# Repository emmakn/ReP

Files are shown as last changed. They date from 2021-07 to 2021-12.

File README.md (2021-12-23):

# ReP
**Re**petative **P**ipettor

## Background
The ReP was created to automate repetative pipetting tasks in a simple and cost-effective way. It utilizes a rack and pinion design to move the pipette's plunger up and down. It can be calibrated to aspirate and dispense at any given rate, frequency, and volume. It is intended to be held upright with a ring stand clamp or any other clamped arm to allow for easy maneuverability and adaptability. The ReP is built around an Eppendorf pipette. The DC motor is controlled with a Raspberry Pi Nano and an L298N motor controller. The structure itself is 3D printed from PLA.

## Included
In this repository, I have included:
1. STL files for the 3D prints,
2. wiring and construction guides, and
3. the code for the raspberry pi

## 1. 3D Printing
There are seven total pieces that need to be printed: *axle_extension, motor_holder_clip_side1_assembly, clip_side2_c, housing, pinion,* and *rack_assembly.* All of the STL files are in the STL folder. None of the pieces require any special printing instructions. PLA is the recommended material given its structural stability and cost. Support material will be required. 20% infill and 0.2 layer height is adequate. Once the piecees have finished printing, thuroughly remove all of the support material especially around the dove tails. 

## 2. Wiring and Construction
The final hardware diagram and orientation of 3D printed parts are shown in Figures 1 and 2, respectively. The following guide will walk through the process of wiring and constructing step by step.

1. Solder pins 16, 18, 20, and 22 onto the Nano.
2. Either hot glue, super glue, or screw the motor controller and Raspberry Pi Nano onto the *clip_side1_c* such that the corners line up with the protrusions on either side of the part. When attaching, be sure the the Nano is facing such that the SD card is facing up and the USB and HDMI ports are facing out. For the motor controller, the heat sink should be facing down. If gluing, make sure to allow the piece to sit for a minute or so to fully dry.
3. Attach all wires as shown in the hardware diagram in Figure 1. The wires leading to the motor can remain unattached for now.

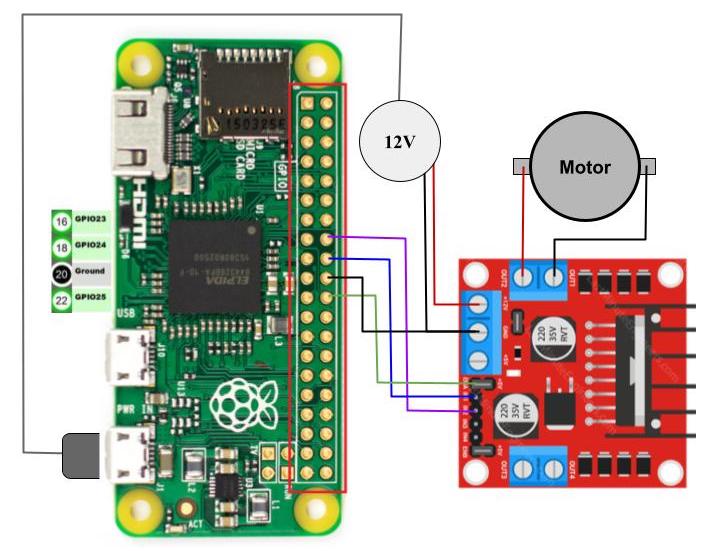
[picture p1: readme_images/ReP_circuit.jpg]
\
*Figure 1: Hardware Diagram*

4. Remove all support material from the 3D printed parts. May need to dremel parts down as necessary depending on printing accuracy.
5. Insert the motor into the *motor_holder* with the axle lined up with the top dove groove.
6. Put the *rack_assembly* into the *housing* and line up the *pinion* inside it as well.
7. Carefully slide the *housing* with the *rack_assembling* and *pinion* into the top dove groove of the *motor_holder*. It is important to line up the flat edge of the pinion with the flat edge of the motor's axle and may take some finessing.
8. Slide *clip_slide1_c* into the bottom groove of the *motor_holder*.

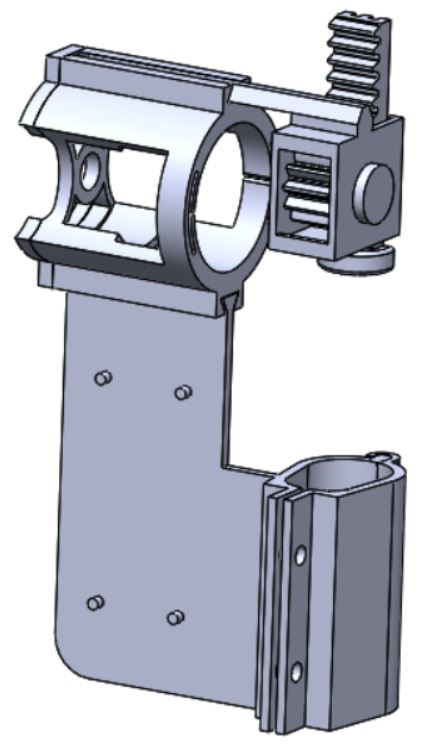
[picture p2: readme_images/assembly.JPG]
\
*Figure 2: Assembly of 3D printed parts.*

10. Attach the two leads from the motor controller to the two nodes on the motor. Figuring out which wire goes to which node will need to be determined by trial and error. If the wires are connected to the wrong nodes, the motor will simply rotate in the opposite direction. The correct orientation will need to be tested by running the up or down program to ensure it goes the correct direction. If the plunger goes down when the up program is ran, simply switch the wires.

## 3. Code
The code must be uploaded to the raspberry pi. I save all of my codes in a folder on the Desktop for easy access. This can be done manually through a USB drive or by remotely accessing the pi and transfering the files through an app such as Transit. I have included a sample code that has an up, down, stop, and loop function that asperates and dispenses 100 ul at a rate of 100 reps per 5 minutes (or 1 rep per 3 seconds) for 15 minutes. It will need to be calibrated to each pipette specifically and will most likely differ slightly from pipette to pipette. Once the code is loaded onto the pi, the following code can be used to run the ReP code provided. 
~~~
cd Desktop/code/
sudo python ReP_code.py
~~~
If you need to edit the code, the following line can be used to edit the code within the terminal.
~~~
nano ReP_code.py
~~~
A futher explanation of the code provided is in the code/README and there are comments annotated in the code itself.

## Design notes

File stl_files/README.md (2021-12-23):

# STL files

The provided STL files are all required to be printed once to create the ReP. These STL files can be uploaded into any 3D printing program for plate placement and slicing. I recommend PLA as the printing material and no special printing instructions are necessary. Defaults of 20% infill and .2 layer height can be used. All of these files were originally created using Solidworks.

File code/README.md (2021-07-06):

# Code

ReP_code.py is broken up into an intro and 5 functinos.

## Intro
~~~
#!/user/bin/env python
import RPi.GPIO as GPIO
import time

# set up pins
in1 = 24
in2 = 23
en = 25
~~~
The intro defines the environment, imports the GPIO and time libraries, and defines the pins used.

## Function 1: setup
~~~
def setup():
    GPIO.setmode(GPIO.BCM)
    GPIO.setup(in1,GPIO.OUT)
    GPIO.setup(in2,GPIO.OUT)
    GPIO.setup(en,GPIO.OUT)
    GPIO.output(in1,GPIO.LOW)
    GPIO.output(in2,GPIO.LOW)
~~~
The setup function defines the pins as BCM and outputs and sets them to "off" (LOW) to start.

## Function 2: print_message
~~~
def print_message():
    print("\nl-loop s-stop u-up d-down Ctrl+C-quit\n")
~~~
These are the 5 keyboard commands that can be used in the program to run different commands. This is the messasge printed in the terminal for the user to see and use as a reference.

## Function 3: destroy
~~~
def destroy():
    GPIO.output(en,GPIO.LOW)
    GPIO.cleanup()
~~~
This will end the program.

## Function 4: main
~~~
def main():
    print_message()
    p=GPIO.PWM(en,1000)
    p.start(50) # motor does not consistently work below 50
    try:
        while(1):
            x = raw_input()
            if x=='l':
                for i in range(300): # 100 equals 5 minutes
                    print("cycle " + str(i+1))
                    # up
                    p.ChangeDutyCycle(50)
                    GPIO.output(in1,GPIO.LOW)
                    GPIO.output(in2,GPIO.HIGH)
                    time.sleep(1.15)
                    # down
                    p.ChangeDutyCycle(55)
                    GPIO.output(in1,GPIO.HIGH)
                    GPIO.output(in2,GPIO.LOW)
                    time.sleep(1.3)
                    # pause
                    GPIO.output(in1,GPIO.LOW)
                    time.sleep(.55)
                x=='z'
            elif x=='s':
                print("stop")
                GPIO.output(in1,GPIO.LOW)
                GPIO.output(in2,GPIO.LOW)
                x=='z'
            elif x=='u':
                print("up")
                GPIO.output(in1,GPIO.LOW)
                GPIO.output(in2,GPIO.HIGH)
                x=='z'
            elif x=='d':
                print("down")
                GPIO.output(in1,GPIO.HIGH)
                GPIO.output(in2,GPIO.LOW)
                x=='z'
            else:
                print("that is not a recognized command, please use one of the commands listed below:\n")
                print_message()
    except KeyboardInterrupt:
        destroy()
~~~
This is the main code that is run when the program is initiated. It contains the 3 previously defined functions. The two settings that are mainly used to calibrate the code to a given pipette are:
~~~
p.ChangeDutyCycle()
time.sleep()
~~~
The DutyCycle determines the percentage of power given to the motor. Our motor did not work consistently below 50% power. The more power that is supplied, the faster the motor goes. The sleep time determines how long each command runs. Between these two commands you can determine speed and duration.

The loop command was developed with the intent to breakup parasitic worms in solution down to the cellular level. The protocol required the solution to be mixed at a consistent rate of one repetition per 3 seconds (or 100 reps per 5 min) for at least 15 minutes.

The stop command stops the motor without exiting the program.

The up and down commands move the plunger up and down.

KeyboardInterrupt is Ctrl+C which exits the entire program.

## Function 5: __name__ = '__main__'
~~~
if __name__ == '__main__':
    setup()
    try:
        main()
    except KeyboardInterrupt:
        destroy()
~~~
This function will run the main function when the following command is entered in the terminal:
~~~
sudo python ReP_code.py
~~~

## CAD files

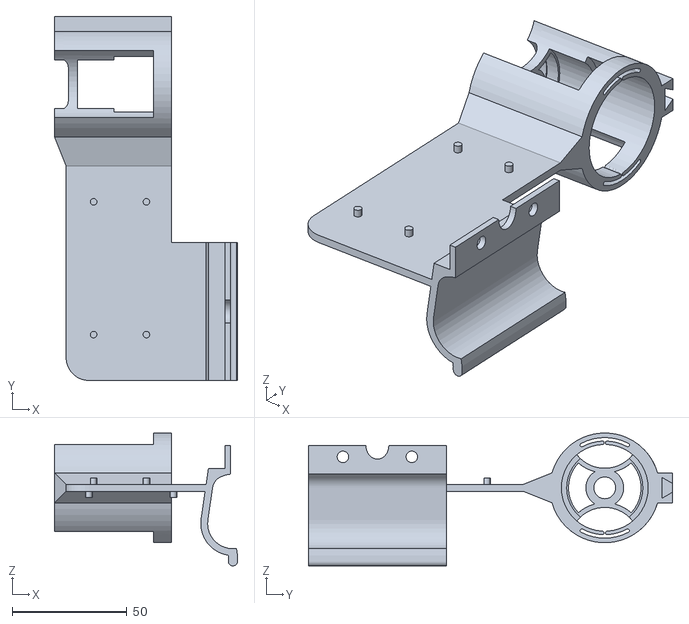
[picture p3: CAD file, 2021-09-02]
stl_files/motor_holder_clip_side1_assembly.STL
79.7 x 158.5 x 57.9

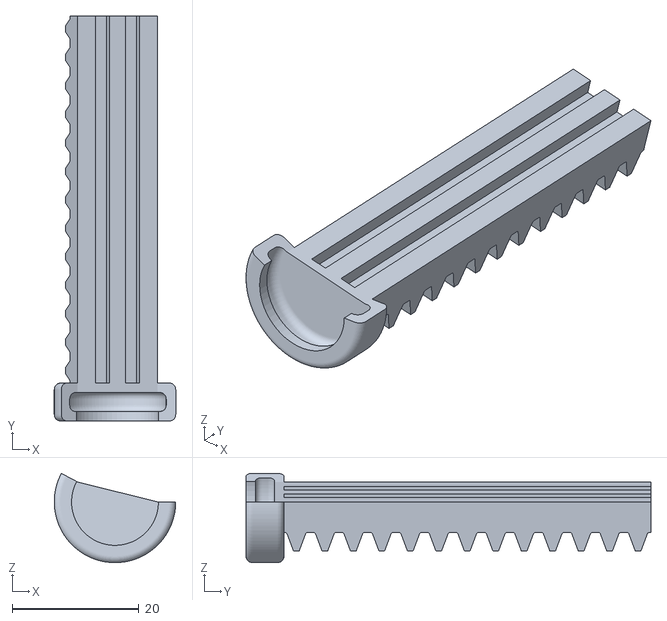
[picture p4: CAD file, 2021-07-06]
stl_files/rack_assembly.STL
19.2 x 64.0 x 14.1

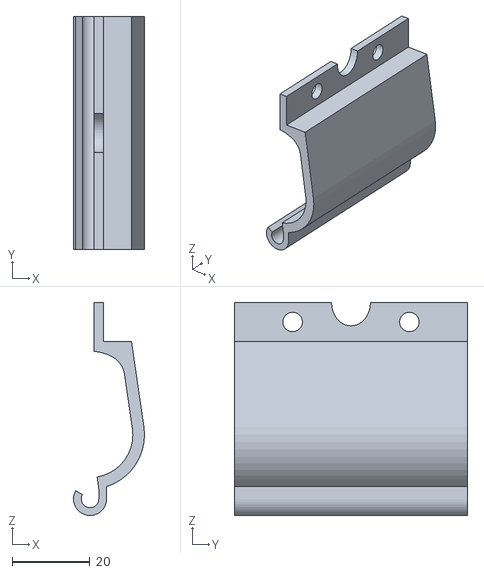
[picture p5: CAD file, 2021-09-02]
stl_files/clip_side2_c.STL
18.2 x 60.0 x 54.8

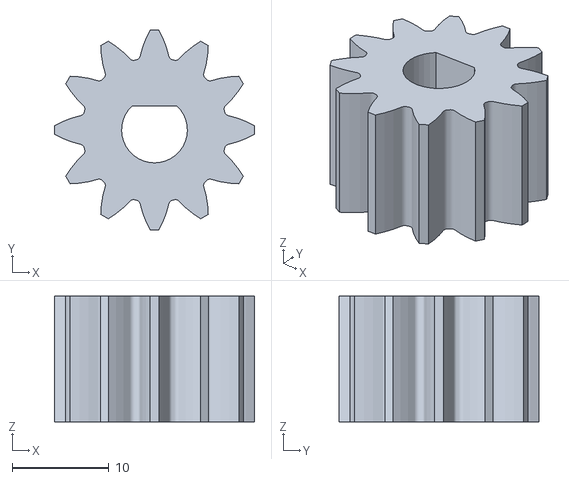
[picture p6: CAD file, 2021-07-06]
stl_files/pinion.STL
20.7 x 20.7 x 13.0

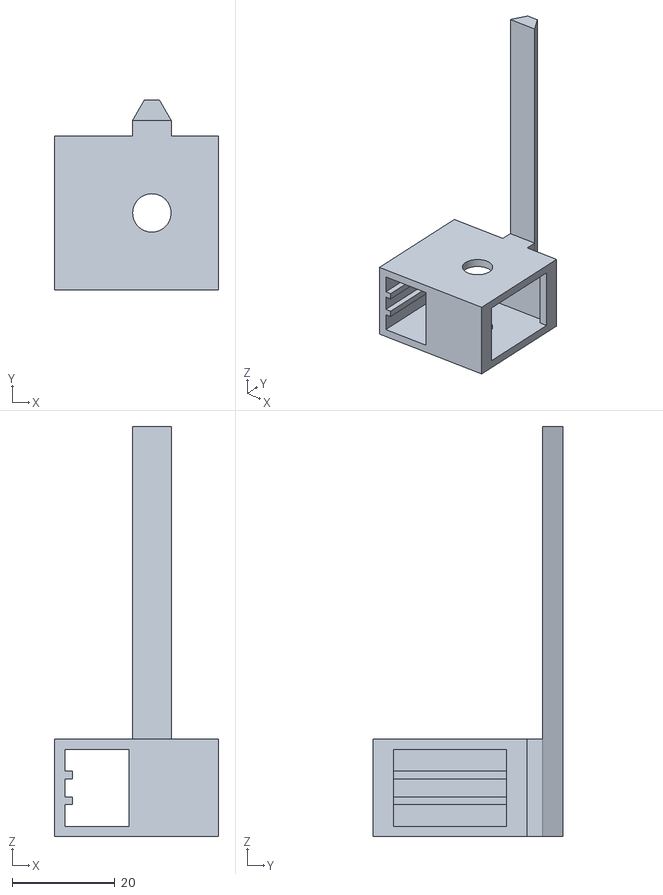
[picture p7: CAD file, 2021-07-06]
stl_files/housing.STL
32.0 x 37.0 x 80.0

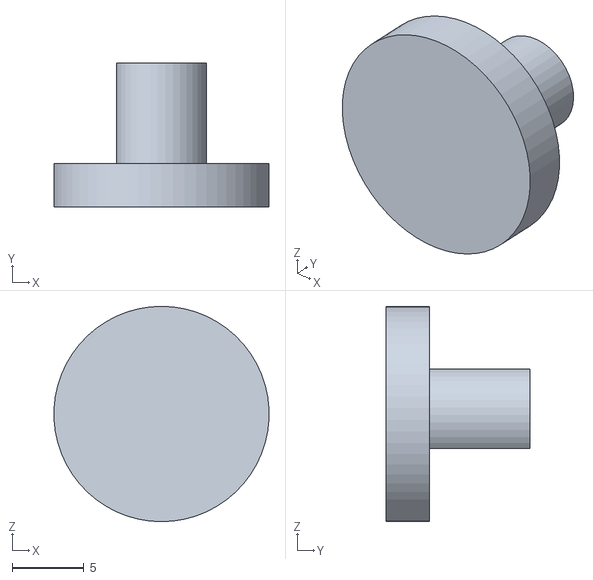
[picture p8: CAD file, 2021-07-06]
stl_files/axle_extension.STL
15.0 x 10.0 x 15.0
